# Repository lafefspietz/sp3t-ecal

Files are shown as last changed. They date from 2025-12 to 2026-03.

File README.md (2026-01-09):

# [sp3t-ecal](https://github.com/lafefspietz/sp3t-ecal)

Open source MEMS-based single pole three throw circuit board with improved impedance matching and SMA launches. This is in a rough draft status now, and is in active development.  This is to become a part of a system which will have two of these switch boards and a set of breakout baords for connecting the DC control lines to these RF switch boards, and to then connect to the 25 pin mirco D which is standard in most cryogenic systems used for superconducting quantum systems. Board is 50 mm square. 
 
 - [SP3TECAL.kicad_sch](SP3TECAL.kicad_sch)
 - [SP3TECAL.kicad_pcb](SP3TECAL.kicad_pcb)
 - [SP3TECAL.kicad_pro](SP3TECAL.kicad_pro)
 - [MM5230-03NDB-TR.lib](MM5230-03NDB-TR.lib)
 - [lafe_spietz_library.kicad_sym](lafe_spietz_library.kicad_sym)

## Screen shot of schematic draft:

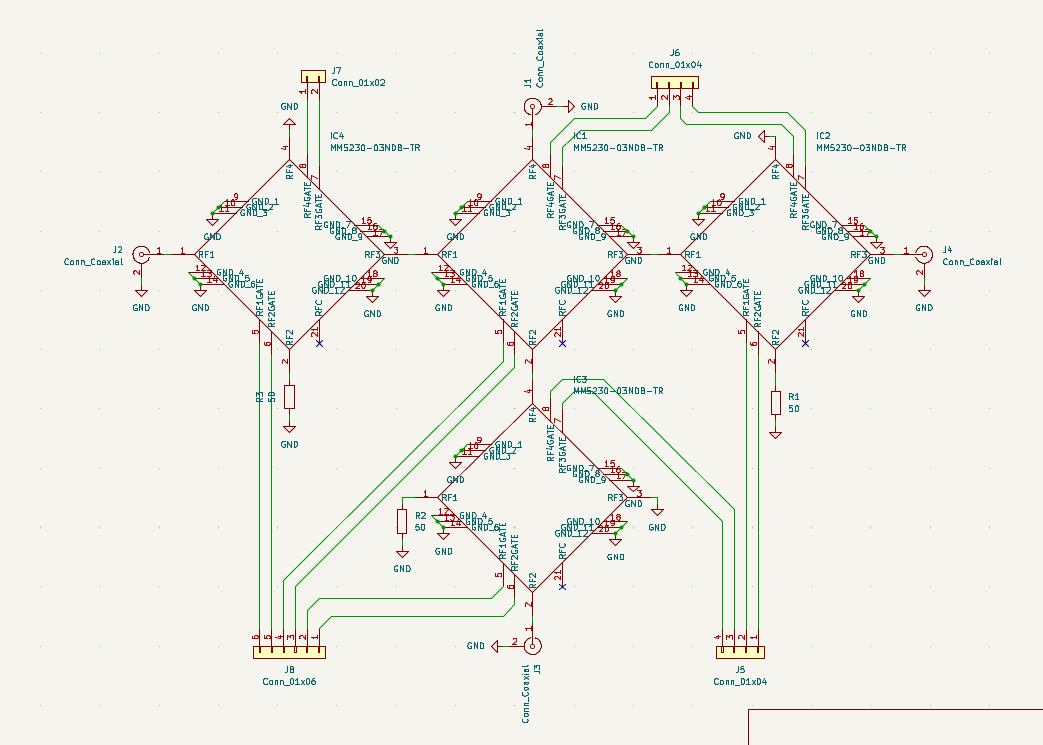
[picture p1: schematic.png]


## Screen shot of layout draft:

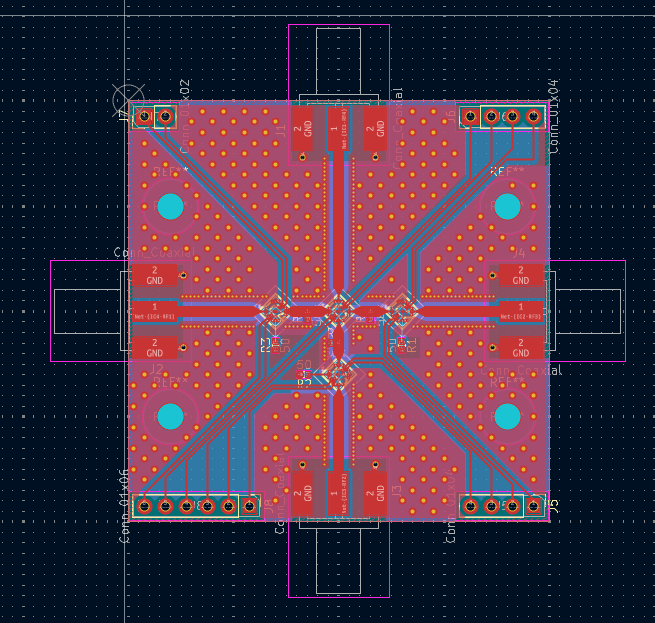
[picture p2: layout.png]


## Screen shot of 3d:

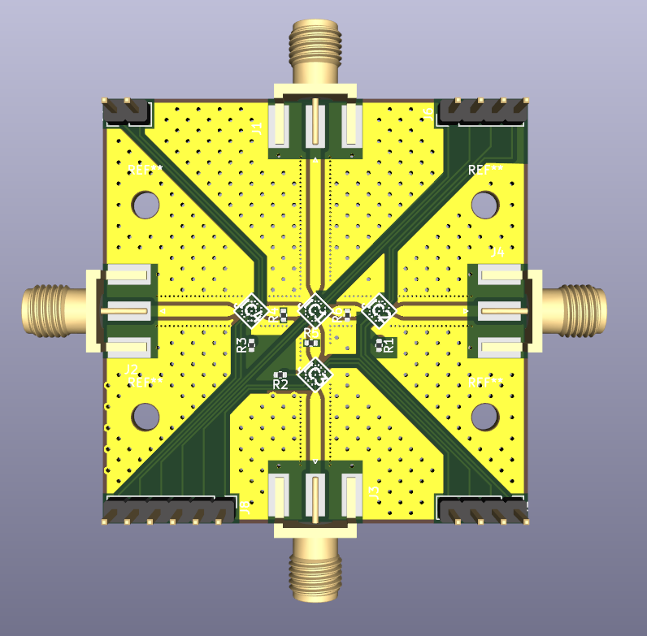
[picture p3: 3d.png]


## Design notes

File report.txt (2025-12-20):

Info: Processing symbol 'IC1:mm5230:MM523003NDB'.
Info: Processing symbol 'IC4:mm5230:MM523003NDB'.
Info: Processing symbol 'IC3:mm5230:MM523003NDB'.
Info: Processing symbol 'IC2:mm5230:MM523003NDB'.
Info: Processing symbol 'J1:Connector_Coaxial:SMA_Molex_73251-1153_EdgeMount_Horizontal'.
Info: Processing symbol 'J2:Connector_Coaxial:SMA_Molex_73251-1153_EdgeMount_Horizontal'.
Info: Processing symbol 'J3:Connector_Coaxial:SMA_Molex_73251-1153_EdgeMount_Horizontal'.
Info: Processing symbol 'J4:Connector_Coaxial:SMA_Molex_73251-1153_EdgeMount_Horizontal'.
Info: Processing symbol 'J5:Connector_PinHeader_2.54mm:PinHeader_1x04_P2.54mm_Vertical'.
Info: Total warnings: 0, errors: 0.
Info: Processing symbol 'J6:Connector_PinHeader_2.54mm:PinHeader_1x04_P2.54mm_Vertical'.
Info: Processing symbol 'J7:Connector_PinHeader_2.54mm:PinHeader_1x02_P2.54mm_Vertical'.
Info: Processing symbol 'J8:Connector_PinHeader_2.54mm:PinHeader_1x06_P2.54mm_Vertical'.
Info: Processing symbol 'R1:Resistor_SMD:R_0402_1005Metric'.
Info: Processing symbol 'R2:Resistor_SMD:R_0402_1005Metric'.
Info: Processing symbol 'R3:Resistor_SMD:R_0402_1005Metric'.
Add net unconnected-(IC1-RFC-Pad21).
Connected IC1 pin 21 to unconnected-(IC1-RFC-Pad21).
Connected IC1 pin 20 to GND.
Connected IC1 pin 15 to GND.
Connected IC1 pin 12 to GND.
Connected IC1 pin 13 to GND.
Connected IC1 pin 11 to GND.
Add net Net-(IC1-RF4).
Connected IC1 pin 4 to Net-(IC1-RF4).
Connected IC1 pin 9 to GND.
Connected IC1 pin 16 to GND.
Add net Net-(IC1-RF2GATE).
Connected IC1 pin 6 to Net-(IC1-RF2GATE).
Add net Net-(IC1-RF1).
Connected IC1 pin 1 to Net-(IC1-RF1).
Connected IC1 pin 19 to GND.
Connected IC1 pin 10 to GND.
Add net Net-(IC1-RF4GATE).
Connected IC1 pin 8 to Net-(IC1-RF4GATE).
Add net Net-(IC1-RF1GATE).
Connected IC1 pin 5 to Net-(IC1-RF1GATE).
Add net Net-(IC1-RF3GATE).
Connected IC1 pin 7 to Net-(IC1-RF3GATE).
Connected IC1 pin 18 to GND.
Add net Net-(IC1-RF2).
Connected IC1 pin 2 to Net-(IC1-RF2).
Connected IC1 pin 14 to GND.
Added IC2 (footprint 'mm5230:MM523003NDB').
Changed IC** reference designator to IC2.
Changed IC2 value from MM523003NDB to MM5230-03NDB-TR.
Updated IC2 symbol association from  to /79b07022-50ec-483d-a1f6-b503f59ca772.
Updated IC2 fields.
Updated IC2 sheetname to '/'.
Updated IC2 sheetfile to 'SP3TECAL.kicad_sch'.
Connected IC2 pin 4 to GND.
Connected IC2 pin 16 to GND.
Connected IC2 pin 19 to GND.
Connected IC2 pin 15 to GND.
Add net unconnected-(IC2-RFC-Pad21).
Connected IC2 pin 21 to unconnected-(IC2-RFC-Pad21).
Connected IC2 pin 20 to GND.
Connected IC2 pin 11 to GND.
Add net Net-(IC2-RF2).
Connected IC2 pin 2 to Net-(IC2-RF2).
Connected IC2 pin 13 to GND.
Connected IC2 pin 14 to GND.
Connected IC2 pin 18 to GND.
Add net Net-(IC2-RF3).
Connected IC2 pin 3 to Net-(IC2-RF3).
Connected IC2 pin 17 to GND.
Add net Net-(IC2-RF3GATE).
Connected IC2 pin 7 to Net-(IC2-RF3GATE).
Connected IC2 pin 10 to GND.
Connected IC2 pin 1 to Net-(IC1-RF3).
Add net Net-(IC2-RF2GATE).
Connected IC2 pin 6 to Net-(IC2-RF2GATE).
Add net Net-(IC2-RF4GATE).
Connected IC2 pin 8 to Net-(IC2-RF4GATE).
Connected IC2 pin 12 to GND.
Connected IC2 pin 9 to GND.
Add net Net-(IC2-RF1GATE).
Connected IC2 pin 5 to Net-(IC2-RF1GATE).
Added IC3 (footprint 'mm5230:MM523003NDB').
Changed IC** reference designator to IC3.
Changed IC3 value from MM523003NDB to MM5230-03NDB-TR.
Updated IC3 symbol association from  to /29d895dc-ca3d-40d6-80b7-e36e3ef9d1bf.
Updated IC3 fields.
Updated IC3 sheetname to '/'.
Updated IC3 sheetfile to 'SP3TECAL.kicad_sch'.
Add net Net-(IC3-RF4GATE).
Connected IC3 pin 8 to Net-(IC3-RF4GATE).
Connected IC3 pin 15 to GND.
Connected IC3 pin 16 to GND.
Connected IC3 pin 13 to GND.
Connected IC3 pin 19 to GND.
Connected IC3 pin 12 to GND.
Connected IC3 pin 3 to GND.
Connected IC3 pin 4 to Net-(IC1-RF2).
Connected IC3 pin 18 to GND.
Add net Net-(IC3-RF2GATE).
Connected IC3 pin 6 to Net-(IC3-RF2GATE).
Add net Net-(IC3-RF2).
Connected IC3 pin 2 to Net-(IC3-RF2).
Connected IC3 pin 10 to GND.
Add net Net-(IC3-RF1GATE).
Connected IC3 pin 5 to Net-(IC3-RF1GATE).
Add net Net-(IC3-RF3GATE).
Connected IC3 pin 7 to Net-(IC3-RF3GATE).
Connected IC3 pin 20 to GND.
Add net Net-(IC3-RF1).
Connected IC3 pin 1 to Net-(IC3-RF1).
Connected IC3 pin 9 to GND.
Add net unconnected-(IC3-RFC-Pad21).
Connected IC3 pin 21 to unconnected-(IC3-RFC-Pad21).
Connected IC3 pin 11 to GND.
Connected IC3 pin 14 to GND.
Connected IC3 pin 17 to GND.
Added IC4 (footprint 'mm5230:MM523003NDB').
Changed IC** reference designator to IC4.
Changed IC4 value from MM523003NDB to MM5230-03NDB-TR.
Updated IC4 symbol association from  to /b7327a34-0eed-4b77-b203-db41979b9248.
Updated IC4 fields.
Updated IC4 sheetname to '/'.
Updated IC4 sheetfile to 'SP3TECAL.kicad_sch'.
Connected IC4 pin 19 to GND.
Connected IC4 pin 4 to GND.
Add net Net-(IC4-RF1GATE).
Connected IC4 pin 5 to Net-(IC4-RF1GATE).
Connected IC4 pin 3 to Net-(IC1-RF1).
Add net Net-(IC4-RF4GATE).
Connected IC4 pin 8 to Net-(IC4-RF4GATE).
Connected IC4 pin 17 to GND.
Connected IC4 pin 9 to GND.
Connected IC4 pin 15 to GND.
Add net Net-(IC4-RF3GATE).
Connected IC4 pin 7 to Net-(IC4-RF3GATE).
Add net Net-(IC4-RF2).
Connected IC4 pin 2 to Net-(IC4-RF2).
Connected IC4 pin 18 to GND.
Connected IC4 pin 16 to GND.
Connected IC4 pin 10 to GND.
Add net Net-(IC4-RF1).
Connected IC4 pin 1 to Net-(IC4-RF1).
Add net Net-(IC4-RF2GATE).
Connected IC4 pin 6 to Net-(IC4-RF2GATE).
Connected IC4 pin 14 to GND.
Connected IC4 pin 20 to GND.
Add net unconnected-(IC4-RFC-Pad21).
Connected IC4 pin 21 to unconnected-(IC4-RFC-Pad21).
Connected IC4 pin 11 to GND.
Connected IC4 pin 13 to GND.
Connected IC4 pin 12 to GND.
Added J1 (footprint 'Connector_Coaxial:SMA_Molex_73251-1153_EdgeMount_Horizontal').
Changed REF** reference designator to J1.
Changed J1 value from SMA_Molex_73251-1153_EdgeMount_Horizontal to Conn_Coaxial.
Updated J1 symbol association from  to /1ebad846-3966-41b4-8a19-6f6ed71a6a6d.
Updated J1 fields.
Updated J1 sheetname to '/'.
Updated J1 sheetfile to 'SP3TECAL.kicad_sch'.
Updated J1 footprint filters to '*BNC* *SMA* *SMB* *SMC* *Cinch* *LEMO* *UMRF* *MCX* *U.FL*'.
Connected J1 pin 2 to GND.
Connected J1 pin 2 to GND.
Connected J1 pin 2 to GND.
Connected J1 pin 2 to GND.
Connected J1 pin 2 to GND.
Connected J1 pin 2 to GND.
Connected J1 pin 2 to GND.
Connected J1 pin 2 to GND.
Connected J1 pin 2 to GND.
Connected J1 pin 2 to GND.
Connected J1 pin 1 to Net-(IC1-RF4).
Added IC1 (footprint 'mm5230:MM523003NDB').
Added J2 (footprint 'Connector_Coaxial:SMA_Molex_73251-1153_EdgeMount_Horizontal').
Changed REF** reference designator to J2.
Changed J2 value from SMA_Molex_73251-1153_EdgeMount_Horizontal to Conn_Coaxial.
Updated J2 symbol association from  to /27fcea4c-f501-4247-b093-c1d6868e0dde.
Updated J2 fields.
Updated J2 sheetname to '/'.
Updated J2 sheetfile to 'SP3TECAL.kicad_sch'.
Updated J2 footprint filters to '*BNC* *SMA* *SMB* *SMC* *Cinch* *LEMO* *UMRF* *MCX* *U.FL*'.
Connected J2 pin 2 to GND.
Connected J2 pin 2 to GND.
Connected J2 pin 2 to GND.
Connected J2 pin 2 to GND.
Connected J2 pin 2 to GND.
Connected J2 pin 2 to GND.
Connected J2 pin 2 to GND.
Connected J2 pin 2 to GND.
Connected J2 pin 2 to GND.
Connected J2 pin 1 to Net-(IC4-RF1).
Connected J2 pin 2 to GND.
Changed IC** reference designator to IC1.
Added J3 (footprint 'Connector_Coaxial:SMA_Molex_73251-1153_EdgeMount_Horizontal').
Changed REF** reference designator to J3.
Changed J3 value from SMA_Molex_73251-1153_EdgeMount_Horizontal to Conn_Coaxial.
Updated J3 symbol association from  to /f328728a-7887-45c8-b8ee-f8669c214e65.
Updated J3 fields.
Updated J3 sheetname to '/'.
Updated J3 sheetfile to 'SP3TECAL.kicad_sch'.
Updated J3 footprint filters to '*BNC* *SMA* *SMB* *SMC* *Cinch* *LEMO* *UMRF* *MCX* *U.FL*'.
Connected J3 pin 2 to GND.
Connected J3 pin 2 to GND.
Connected J3 pin 2 to GND.
Connected J3 pin 2 to GND.
Connected J3 pin 1 to Net-(IC3-RF2).
Connected J3 pin 2 to GND.
Connected J3 pin 2 to GND.
Connected J3 pin 2 to GND.
Connected J3 pin 2 to GND.
Connected J3 pin 2 to GND.
Connected J3 pin 2 to GND.
Changed IC1 value from MM523003NDB to MM5230-03NDB-TR.
Added J4 (footprint 'Connector_Coaxial:SMA_Molex_73251-1153_EdgeMount_Horizontal').
Changed REF** reference designator to J4.
Changed J4 value from SMA_Molex_73251-1153_EdgeMount_Horizontal to Conn_Coaxial.
Updated J4 symbol association from  to /17036cbb-d227-466a-93ab-07385caff96b.
Updated J4 fields.
Updated J4 sheetname to '/'.
Updated J4 sheetfile to 'SP3TECAL.kicad_sch'.
Updated J4 footprint filters to '*BNC* *SMA* *SMB* *SMC* *Cinch* *LEMO* *UMRF* *MCX* *U.FL*'.
Connected J4 pin 2 to GND.
Connected J4 pin 1 to Net-(IC2-RF3).
Connected J4 pin 2 to GND.
Connected J4 pin 2 to GND.
Connected J4 pin 2 to GND.
Connected J4 pin 2 to GND.
Connected J4 pin 2 to GND.
Connected J4 pin 2 to GND.
Connected J4 pin 2 to GND.
Connected J4 pin 2 to GND.
Connected J4 pin 2 to GND.
Updated IC1 symbol association from  to /3e218a32-2774-4c0f-9027-a97876643703.
Added J5 (footprint 'Connector_PinHeader_2.54mm:PinHeader_1x04_P2.54mm_Vertical').
Changed REF** reference designator to J5.
Changed J5 value from PinHeader_1x04_P2.54mm_Vertical to Conn_01x04.
Updated J5 symbol association from  to /f404436d-3f46-4256-b1c0-3e453a5987af.
Updated J5 fields.
Updated J5 sheetname to '/'.
Updated J5 sheetfile to 'SP3TECAL.kicad_sch'.
Updated J5 footprint filters to 'Connector*:*_1x??_*'.
Updated IC1 fields.
Connected J5 pin 1 to Net-(IC2-RF2GATE).
Connected J5 pin 2 to Net-(IC2-RF1GATE).
Connected J5 pin 3 to Net-(IC3-RF4GATE).
Updated IC1 sheetname to '/'.
Added J6 (footprint 'Connector_PinHeader_2.54mm:PinHeader_1x04_P2.54mm_Vertical').
Changed REF** reference designator to J6.
Changed J6 value from PinHeader_1x04_P2.54mm_Vertical to Conn_01x04.
Updated J6 symbol association from  to /832f210d-ca62-42c9-ae07-b18432986929.
Updated J6 fields.
Updated J6 sheetname to '/'.
Updated J6 sheetfile to 'SP3TECAL.kicad_sch'.
Updated J6 footprint filters to 'Connector*:*_1x??_*'.
Connected J6 pin 1 to Net-(IC1-RF4GATE).
Connected J6 pin 3 to Net-(IC2-RF4GATE).
Connected J6 pin 4 to Net-(IC2-RF3GATE).
Connected J6 pin 2 to Net-(IC1-RF3GATE).
Updated IC1 sheetfile to 'SP3TECAL.kicad_sch'.
Added J7 (footprint 'Connector_PinHeader_2.54mm:PinHeader_1x02_P2.54mm_Vertical').
Changed REF** reference designator to J7.
Changed J7 value from PinHeader_1x02_P2.54mm_Vertical to Conn_01x02.
Updated J7 symbol association from  to /74eb3e15-3037-411f-b4f9-73643c7e07a5.
Updated J7 fields.
Updated J7 sheetname to '/'.
Updated J7 sheetfile to 'SP3TECAL.kicad_sch'.
Updated J7 footprint filters to 'Connector*:*_1x??_*'.
Connected J7 pin 2 to Net-(IC4-RF3GATE).
Connected J7 pin 1 to Net-(IC4-RF4GATE).
Add net GND.
Added J8 (footprint 'Connector_PinHeader_2.54mm:PinHeader_1x06_P2.54mm_Vertical').
Changed REF** reference designator to J8.
Changed J8 value from PinHeader_1x06_P2.54mm_Vertical to Conn_01x06.
Updated J8 symbol association from  to /dd451948-362f-4ec4-93f2-a2060d5020ad.
Updated J8 fields.
Updated J8 sheetname to '/'.
Updated J8 sheetfile to 'SP3TECAL.kicad_sch'.
Updated J8 footprint filters to 'Connector*:*_1x??_*'.
Connected J8 pin 3 to Net-(IC1-RF2GATE).
Connected J8 pin 6 to Net-(IC4-RF1GATE).
Connected J5 pin 4 to Net-(IC3-RF3GATE).
Connected J8 pin 4 to Net-(IC1-RF1GATE).
Connected J8 pin 1 to Net-(IC3-RF2GATE).
Connected J8 pin 5 to Net-(IC4-RF2GATE).
Connected IC1 pin 17 to GND.
Added R1 (footprint 'Resistor_SMD:R_0402_1005Metric').
Changed REF** reference designator to R1.
Changed R1 value from R_0402_1005Metric to 50.
Updated R1 symbol association from  to /fe68d1b0-03de-4320-9143-be0620085d62.
Updated R1 fields.
Updated R1 sheetname to '/'.
Updated R1 sheetfile to 'SP3TECAL.kicad_sch'.
Updated R1 footprint filters to 'R_*'.
Connected R1 pin 1 to Net-(IC2-RF2).
Connected R1 pin 2 to GND.
Add net Net-(IC1-RF3).
Added R2 (footprint 'Resistor_SMD:R_0402_1005Metric').
Changed REF** reference designator to R2.
Changed R2 value from R_0402_1005Metric to 50.
Updated R2 symbol association from  to /e5142d02-0f26-4246-8df4-91b4493c952f.
Updated R2 fields.
Updated R2 sheetname to '/'.
Updated R2 sheetfile to 'SP3TECAL.kicad_sch'.
Updated R2 footprint filters to 'R_*'.
Connected R2 pin 1 to Net-(IC3-RF1).
Connected R2 pin 2 to GND.
Connected IC1 pin 3 to Net-(IC1-RF3).
Added R3 (footprint 'Resistor_SMD:R_0402_1005Metric').
Changed REF** reference designator to R3.
Changed R3 value from R_0402_1005Metric to 50.
Updated R3 symbol association from  to /e06167e5-f170-494d-868d-d268c2671973.
Updated R3 fields.
Updated R3 sheetname to '/'.
Updated R3 sheetfile to 'SP3TECAL.kicad_sch'.
Updated R3 footprint filters to 'R_*'.
Connected R3 pin 1 to GND.
Connected R3 pin 2 to Net-(IC4-RF2).

Connected J8 pin 2 to Net-(IC3-RF1GATE).

Info: Total warnings: 0, errors: 0.

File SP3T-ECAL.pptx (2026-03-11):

## MM4250 Cal PCBs and Dual SP3T Ecal

Lafe Spietz
NIST
Boulder, CO

## CPW-G Rogers 4350 B 0.762 mm (30 mils)

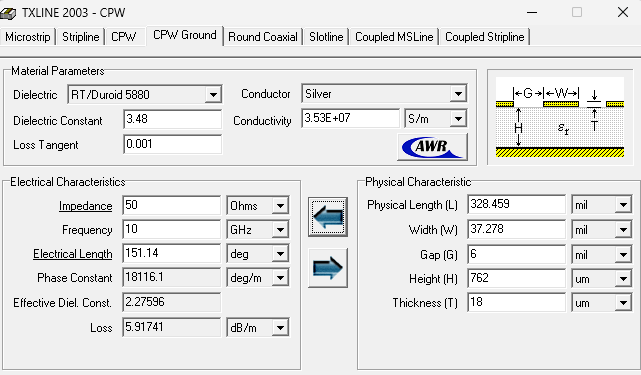
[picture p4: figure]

https://rogerscorp.com/advanced-electronics-solutions/ro4000-series-laminates/ro4350b-laminates

## 60 mil thick board

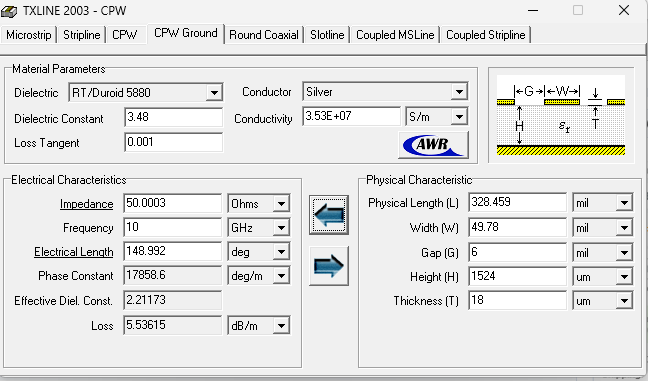
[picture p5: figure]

## Load resistors

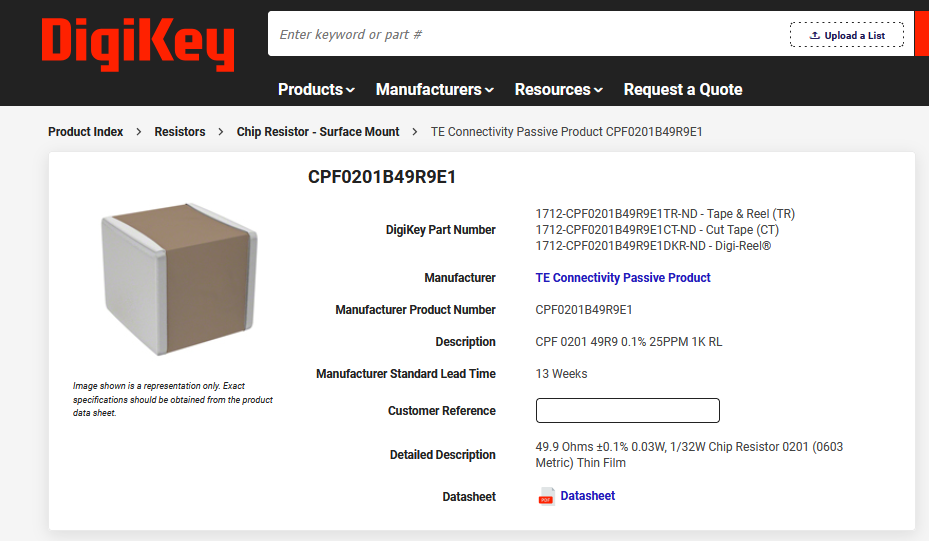
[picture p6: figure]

https://www.digikey.com/en/products/detail/te-connectivity-passive-product/CPF0201B49R9E1/14007284

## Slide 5

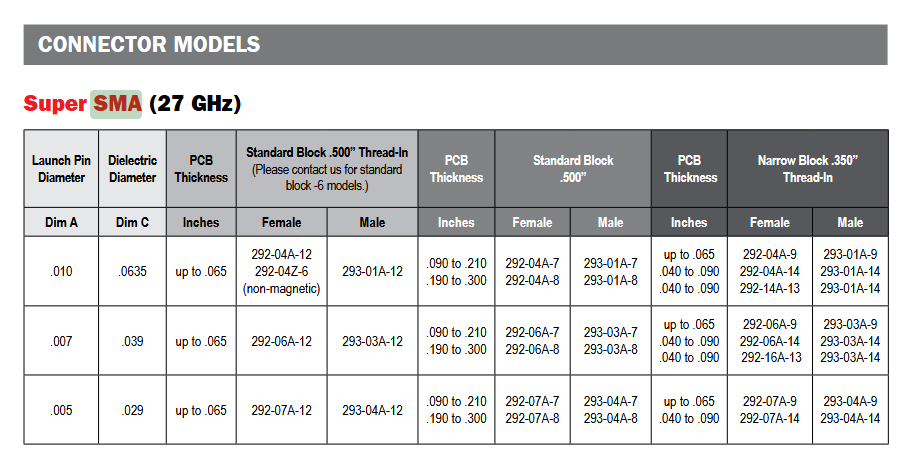
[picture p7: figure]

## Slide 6

https://mpd.southwestmicrowave.com/product/292-04a-12-end-launch-supersma-27-ghz-jack-female-standard-block-500-thread-in/

## SOLT Standards

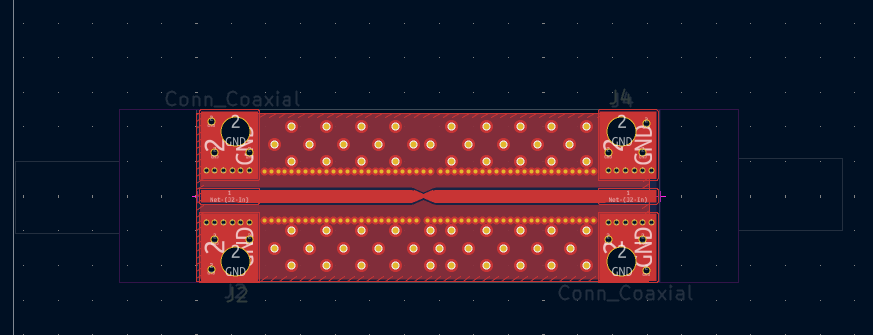
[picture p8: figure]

THRU

SHORT

LOAD

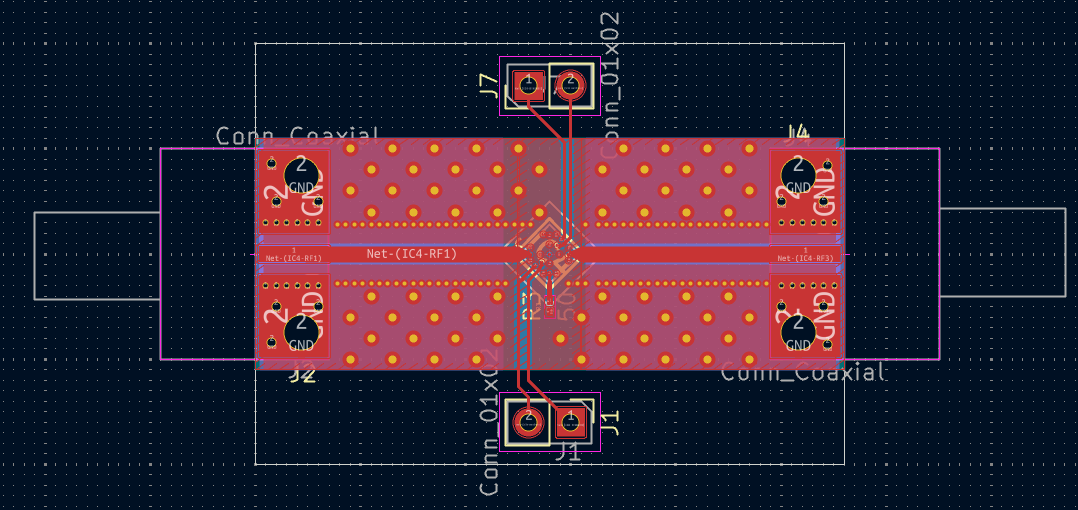
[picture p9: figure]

SWITCH

OPEN

## Dual SP3T Ecal

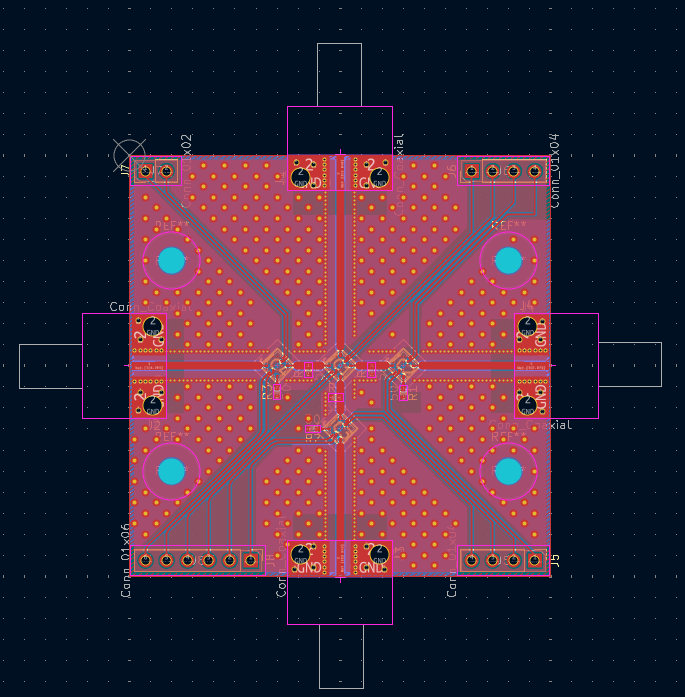
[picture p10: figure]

## Questions

- Do we want to make an attempted impedance transformer to also test?
- Do we want to switch to the full Eurocircuits stackup for the SP3T board?
- Do we want 30 mil or 60 mil boards for the test boards?
- Who orders the boards?
- What else to make?
- What about trying to measure TWPA in existing switch setup? Have they tried it? Should we try it?
- Where to publish results on measurements?

## Impedance matching network, version 1

Input

√((600 pH)/(0.3 pF)) = 44.7 Ω

Switch

0.3 pF

600 pH

## 44.7 Ohm impedance

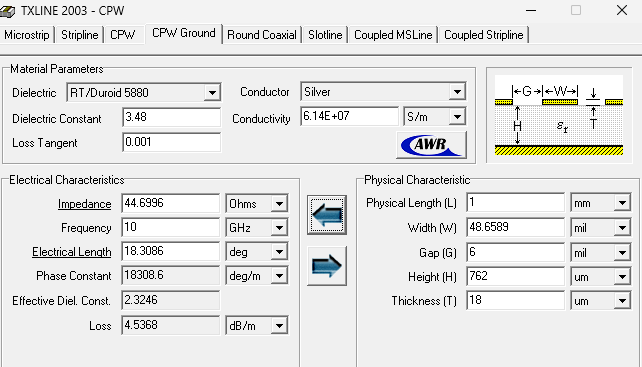
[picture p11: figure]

## We have 4 of these:

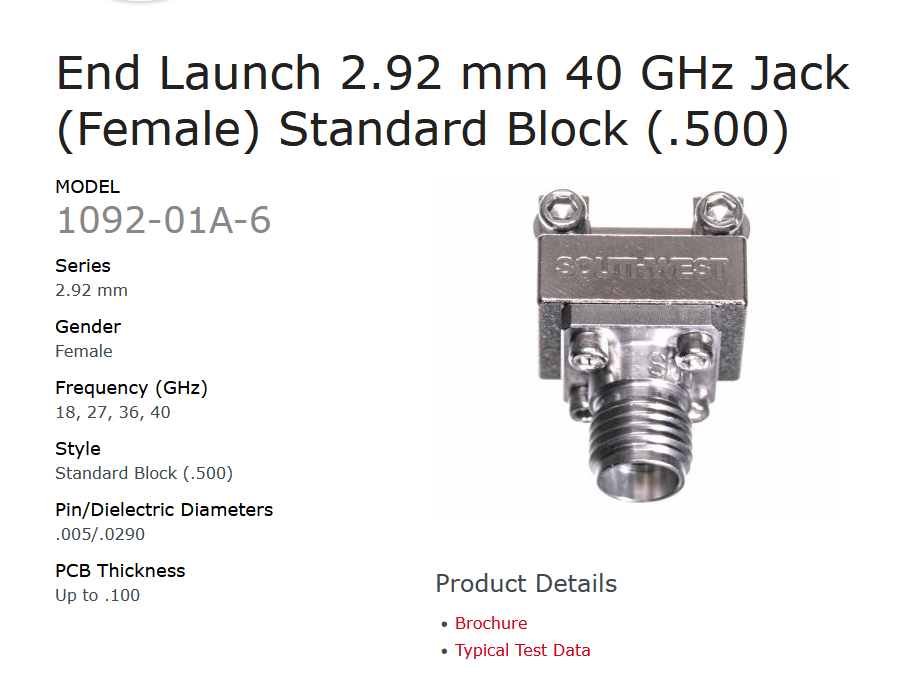
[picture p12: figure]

## TWPA-TRON

SPDT

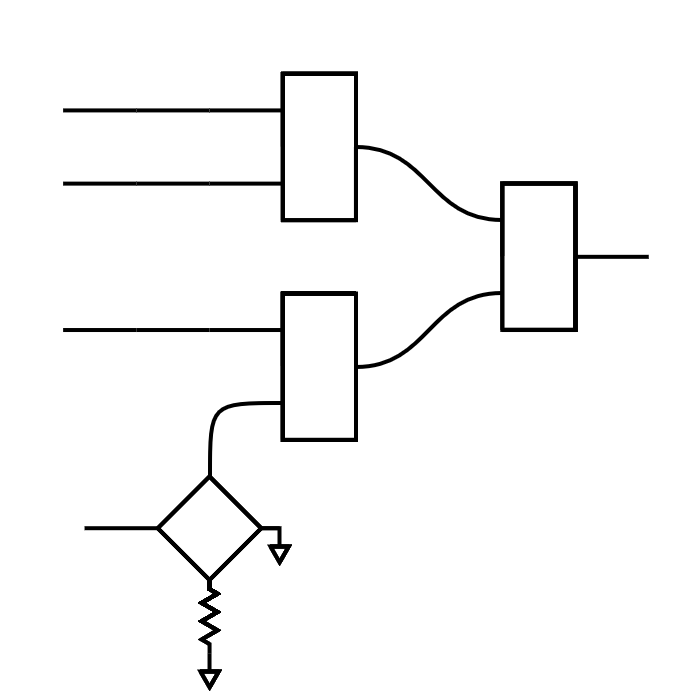
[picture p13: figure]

SPDT

DUT1

SPDT

DUT2

SPDT

SPDT

DUT3

SPDT

SP3T

SP3T

SOLR

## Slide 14

TWPA-TRON

SPDT

DUT1

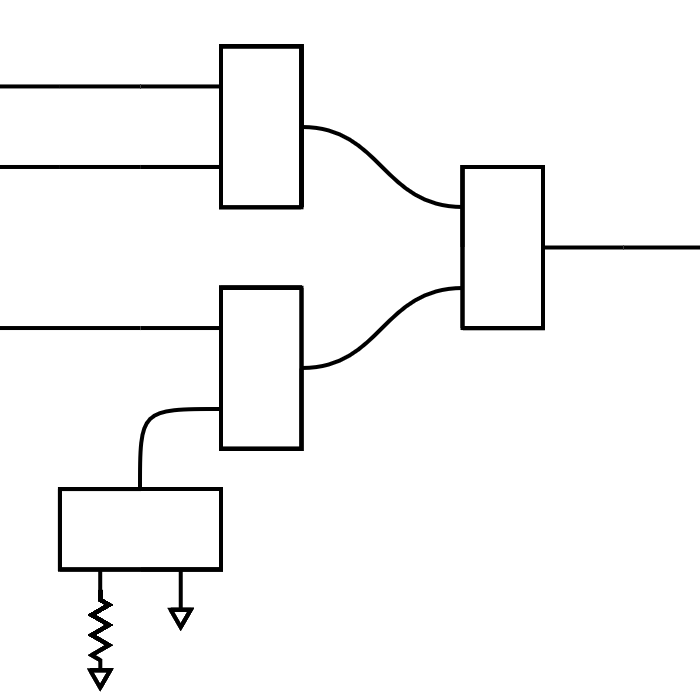
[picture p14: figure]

SPDT

SPDT

DUT2

SPDT

SPDT

SPDT

DUT3

SOL

SPDT

SPDT

SOL

## Rough draft of layout topology

## TWPAtron rough layout topology

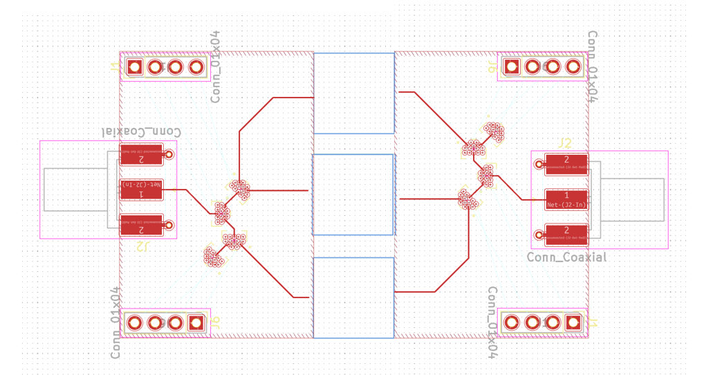
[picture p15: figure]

## TWPAtron Draft

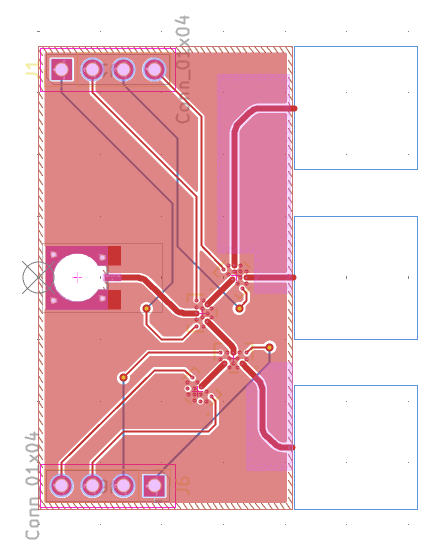
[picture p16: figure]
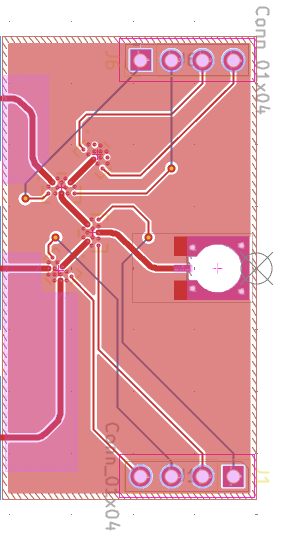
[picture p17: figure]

10x10 mm

## 3d render of latest draft

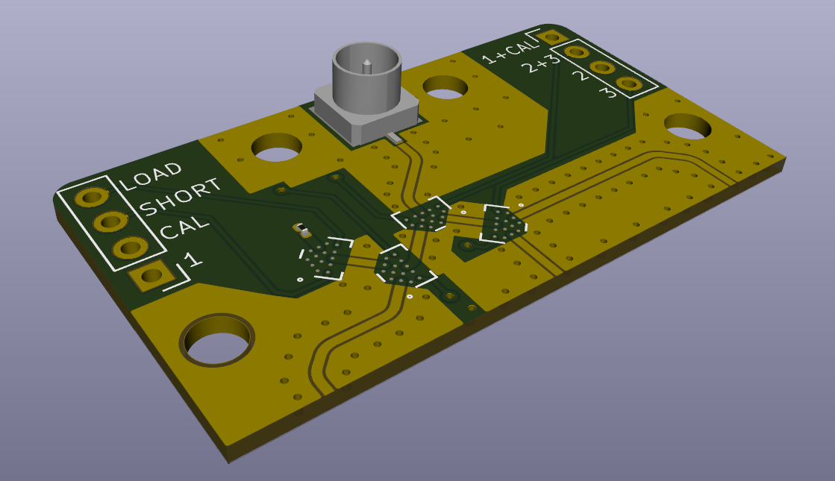
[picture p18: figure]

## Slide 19

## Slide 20

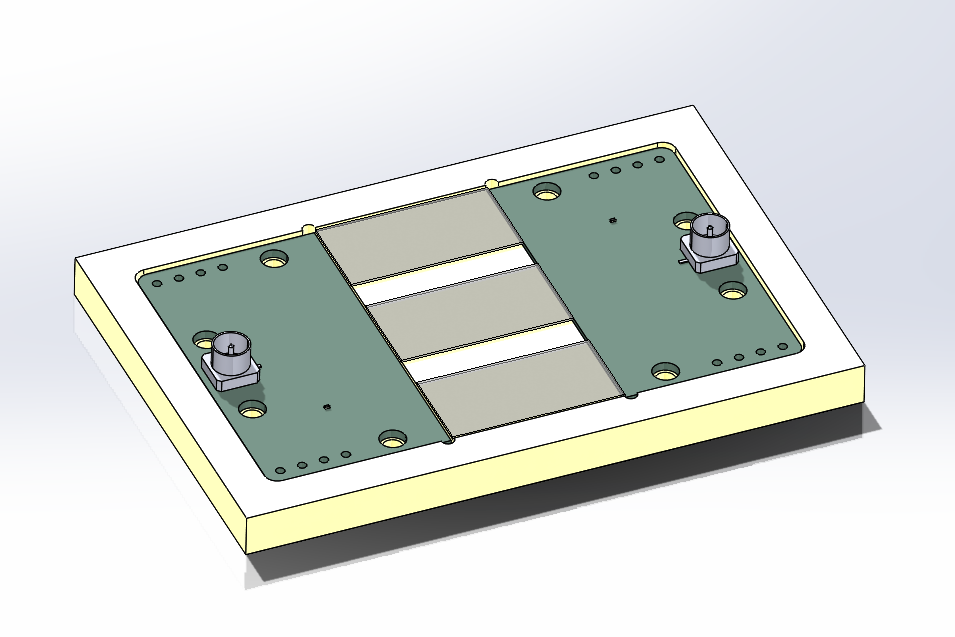
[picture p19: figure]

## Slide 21

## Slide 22

24X65 mil

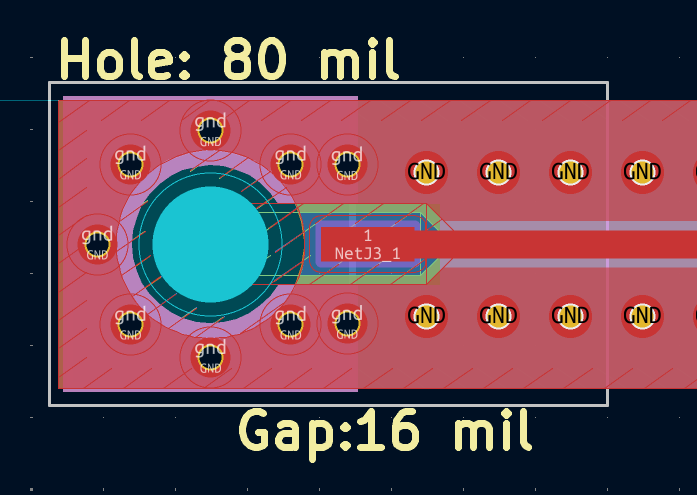
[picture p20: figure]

Diameter 0.131”

Diameter 0.08”

0.085”

0.016”

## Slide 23

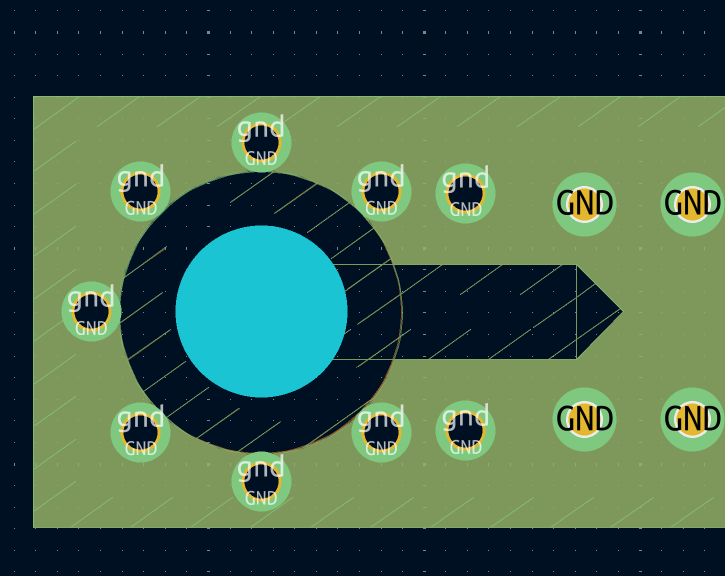
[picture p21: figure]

0.103”

0.044”

## Looking at JAWS designs and Aivon designs

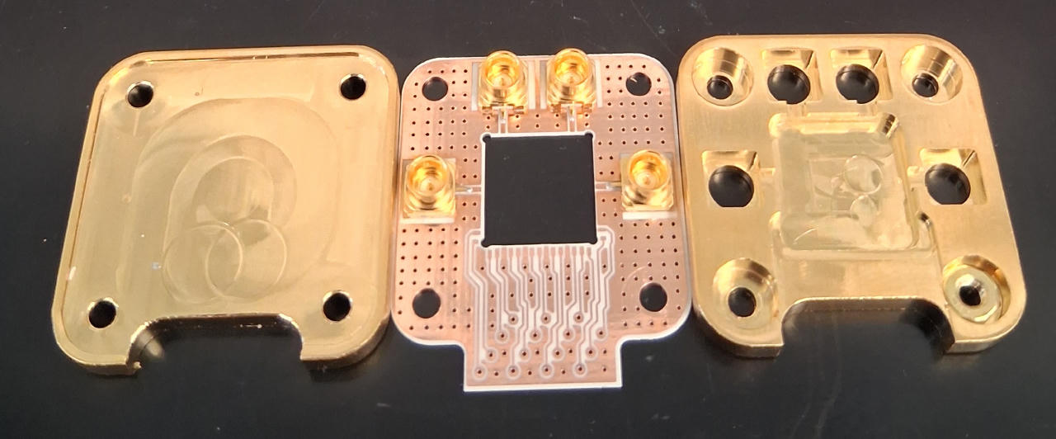
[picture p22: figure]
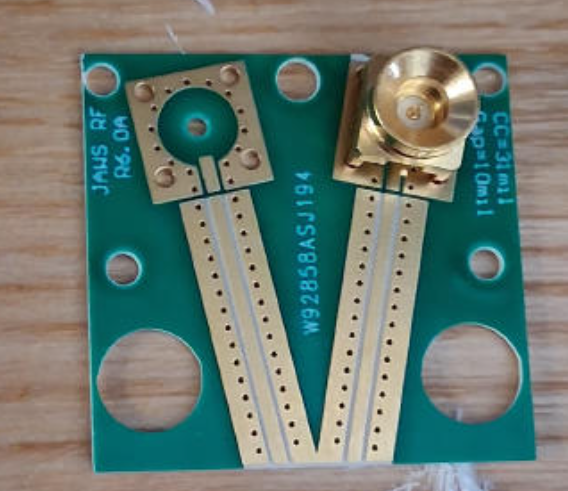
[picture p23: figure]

https://www.digikey.com/en/products/detail/molex/0734153310/2755910

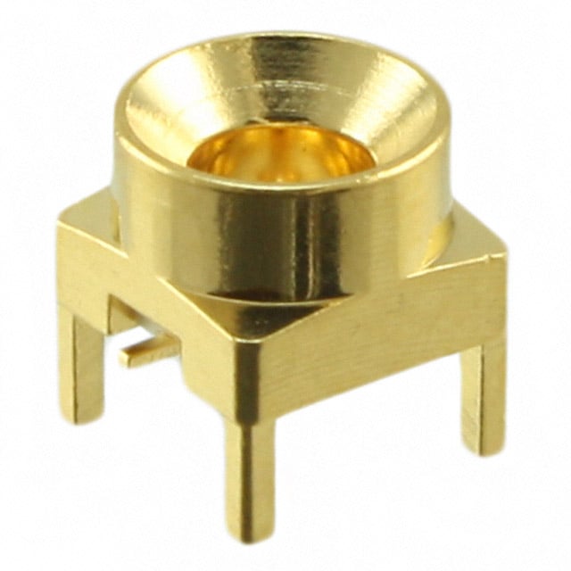
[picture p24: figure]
SMP Connector Plug, Male Pin 50 Ohms Surface Mount Solder

Move to 20 mil PCB
With one insulating layer and 2 copper layers

WM5394CT-ND

## M2.5 Screw and Nut

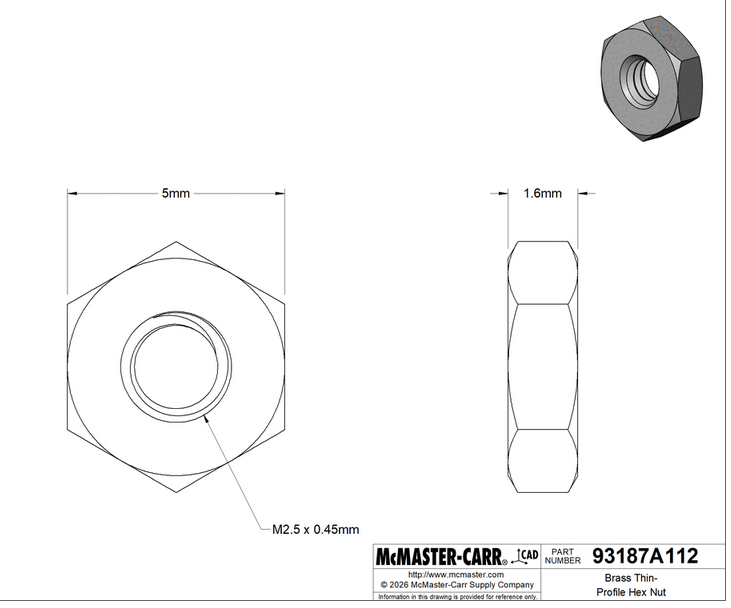
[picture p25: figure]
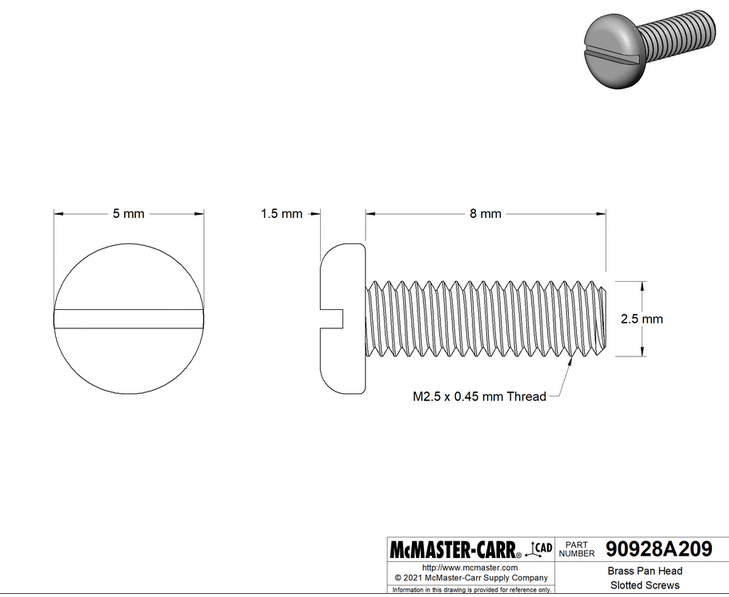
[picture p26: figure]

Clearance 2.75 mm = 108 mils

https://www.mcmaster.com/90928A209/

https://www.mcmaster.com/93187A112/

## JAWS Import from Alium

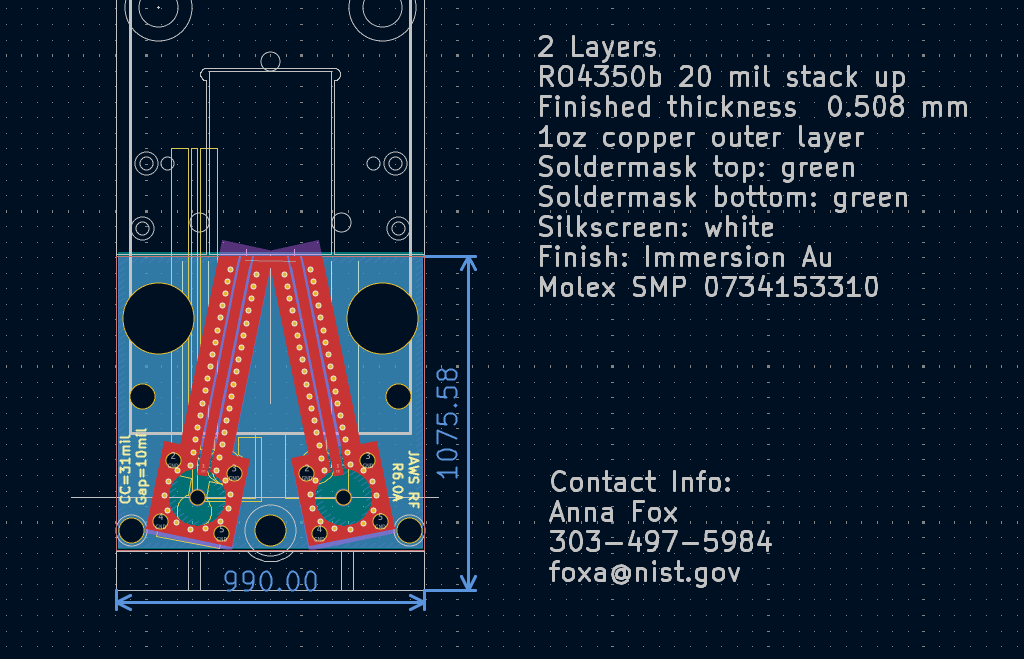
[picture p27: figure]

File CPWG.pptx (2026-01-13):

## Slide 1


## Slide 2

https://rogerscorp.com/advanced-electronics-solutions/ro4000-series-laminates/ro4350b-laminates


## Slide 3


https://mpd.southwestmicrowave.com/wp-content/uploads/End-Launch-Connectors-2024.pdf

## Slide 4


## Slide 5


https://mpd.southwestmicrowave.com/product/292-04a-12-end-launch-supersma-27-ghz-jack-female-standard-block-500-thread-in/

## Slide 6

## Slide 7


https://www.digikey.com/en/products/detail/te-connectivity-linx/CONSMA020-031-G/11482823

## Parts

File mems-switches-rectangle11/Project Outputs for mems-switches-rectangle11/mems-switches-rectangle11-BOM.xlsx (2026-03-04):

Description | Designator | Footprint | Quantity | Mfgr | Mfgr Part No.
DNP | [NoValue], 0 | DNP | 3
DNP | Designator4 | DNP | 1
SMOOTH BORE SMP Connector Plug, Male Pin 50Ohm Surface Mount Solder | J1, J2, J3, J4, J5, J6, J7, J8, J9, J10 | rosenberger-19S201-40ML5 | 10 | Rosenberger | 19S201-40ML5
DNP | J11, J12, J13, J14 | DNP | 4
CPF 0201 56K2 0.1% 25PPM 1K RL | R1, R2, R3, R4, R5, R6, R7, R8, R9, R10, R11, R12 | 0201-resistor | 12 | TE connectivity | CPF0201B56K2E1
High power SP4T MEMs switch | U1, U2, U3, U4 | MM5130-NORM_PCB_NOFLOOD | 4 | Menlo Microwave | MM5130-03NDB-TR

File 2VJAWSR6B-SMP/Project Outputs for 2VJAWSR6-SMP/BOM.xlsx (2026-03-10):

Designator | Qty | Link | MFR | P/N
Designator 19, Designator 20 | 2 | https://www.digikey.com/en/products/detail/molex/0734153310/2755910 | Molex | 734153310

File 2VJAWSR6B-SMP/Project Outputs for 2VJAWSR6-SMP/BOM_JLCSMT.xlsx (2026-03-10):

Comment | Designator | Footprint | JLCPCB Part #（optional）
 | Designator19, Designator20 |  | C5859378

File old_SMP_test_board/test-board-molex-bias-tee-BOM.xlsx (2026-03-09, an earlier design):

Description | Designator | Quantity | Manufacturer Part Number 1 | Mfr_Name | Link
BROADBAND CAPACITOR, 100 nF, 0201 | C1, C2 | 2 | 0201BB104KW160 | Passive Plus | https://www.digikey.com/en/products/detail/passive-plus/0201BB104KW160/19186628
Molex 85305-0232 | J1, J2, J3, J4, J5, J6, J7, J8, J9, J10, J11, J12, J25, J26, J27, J28, J29, J30, J31, J32 | 20 | 85305-0232 | Molex | https://www.digikey.com/en/products/detail/molex/0853050232/2421464
SMP-right-angle-19S201-40ML5 | J13, J14, J15, J16, J17, J18 | 6 | 19S201-40ML5 | Rosenberger | https://www.digikey.com/en/products/detail/rosenberger/19S201-40ML5/7926834
Coilcraft BCR-232 2.35 uH conical inductor | L1, L2, L3 | 3 | BCR-232 | CoilCraft | https://www.coilcraft.com/en-us/products/rf/conical-broadband/0-40-ghz/bcr/bcr-232/

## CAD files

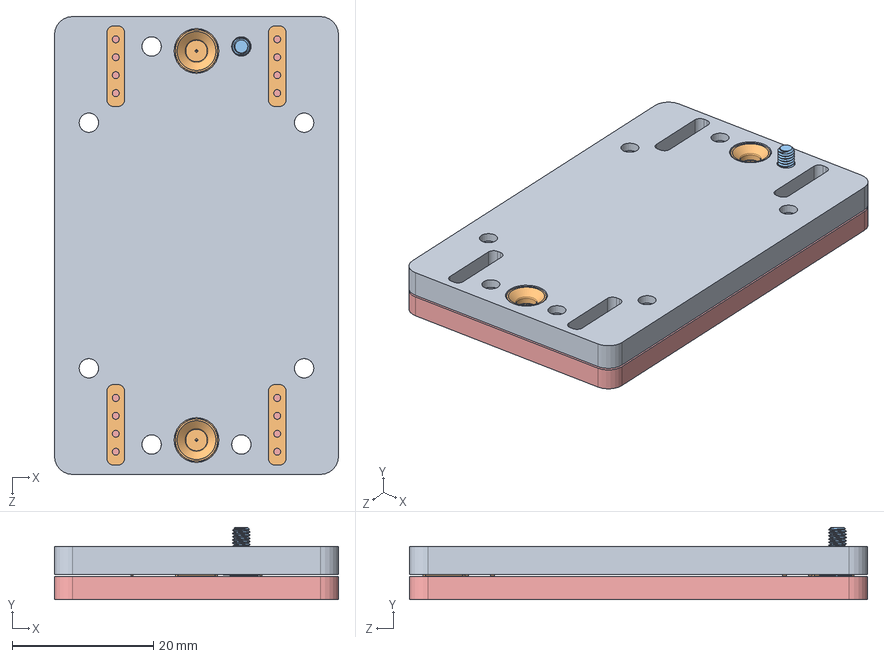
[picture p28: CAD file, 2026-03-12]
twpatron-2-b-assembly.SLDASM
40.2 x 10.3 x 64.8 mm
tpwatron-2-end2
93187A112_Brass Thin-Profile Hex Nut x 2
90928A209_Brass Pan Head Slotted Screws
twpatron-2d x 2
twpatron-lid

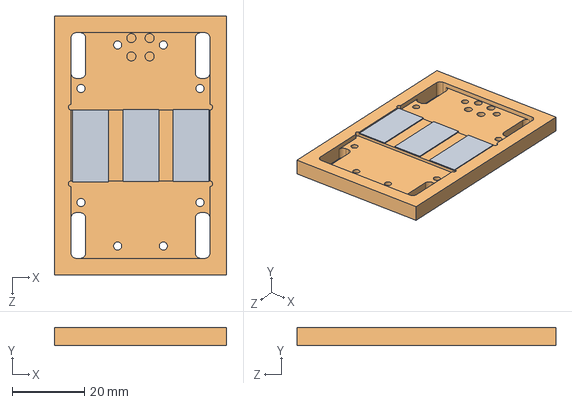
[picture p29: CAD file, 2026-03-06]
twpatron2-Assembly-1.SLDASM
47.8 x 5.00 x 71.8 mm
twpatron-base
chip-10x20 x 3

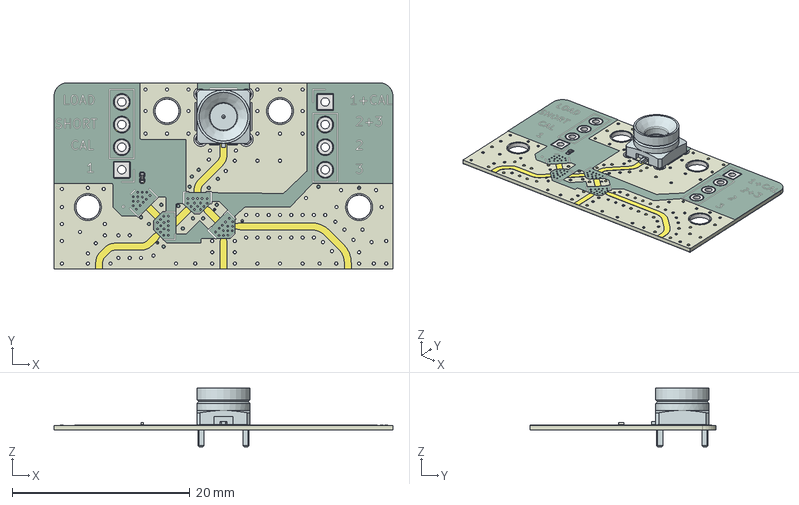
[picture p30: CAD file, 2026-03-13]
twpatron-2e.step
38.1 x 21.0 x 6.60 mm
R_0201_0603Metric
kicad_embedded_6A8167ECC7562BB89ECF910EFD87DB84
twpatron-2_copper
twpatron-2_pad
twpatron-2_via
twpatron-2_silkscreen x 2
twpatron-2_soldermask x 2
twpatron-2_PCB

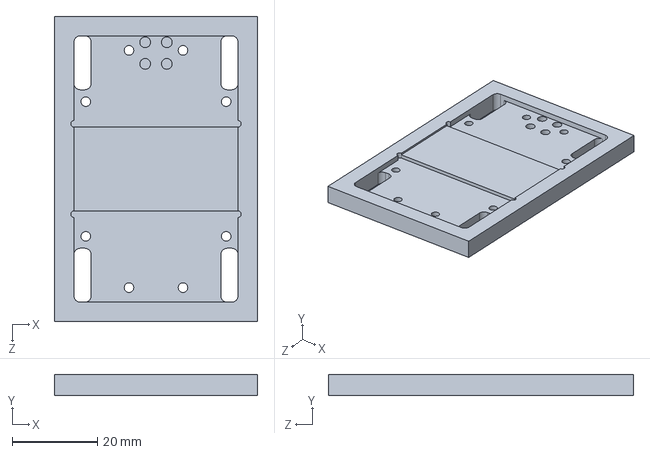
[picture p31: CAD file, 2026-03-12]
twpatron-base.SLDPRT
47.8 x 5.00 x 71.8 mm

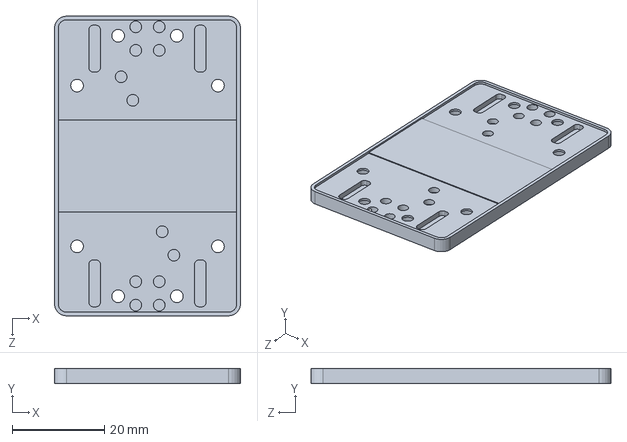
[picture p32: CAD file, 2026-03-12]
tpwatron-2-end2.SLDPRT
40.2 x 3.30 x 64.8 mm

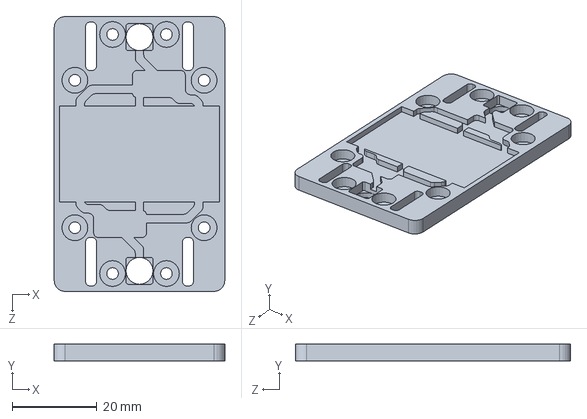
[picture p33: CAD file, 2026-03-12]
twpatron-lid.SLDPRT
40.2 x 3.95 x 64.8 mm

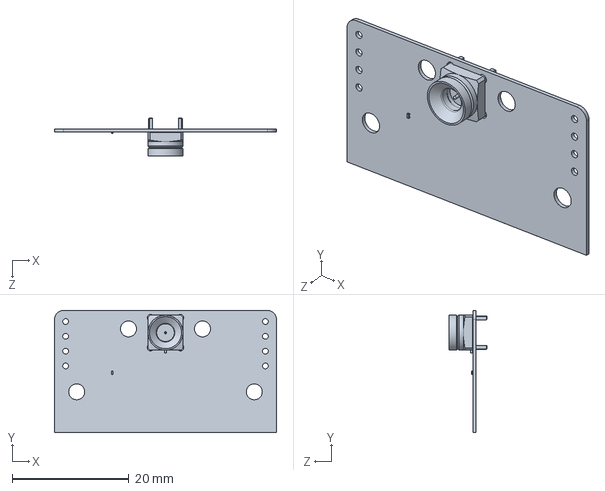
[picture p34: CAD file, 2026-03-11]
twpatron-2b.SLDPRT
38.1 x 21.0 x 6.60 mm

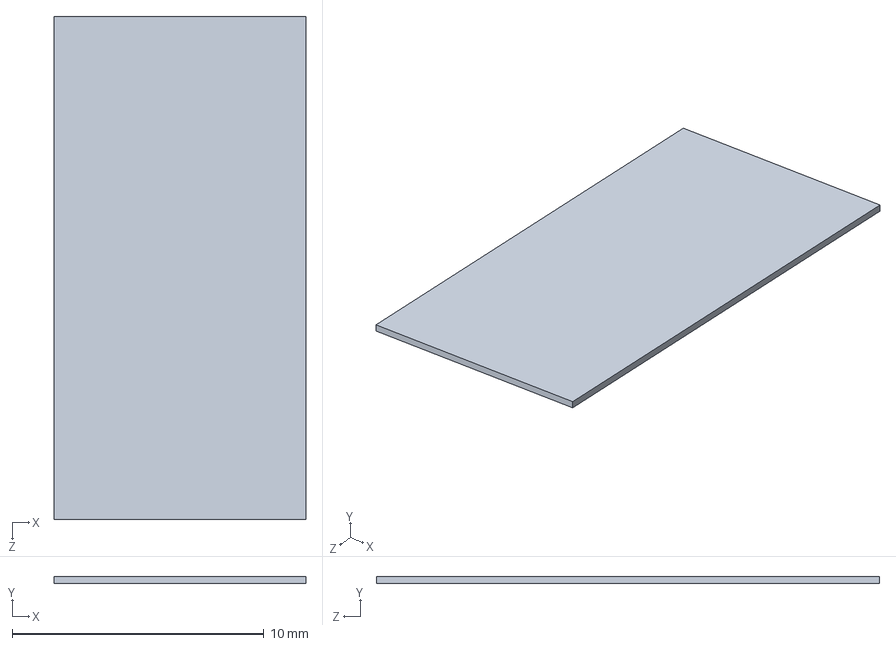
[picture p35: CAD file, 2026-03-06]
chip-10x20.SLDPRT
10.0 x 0.285 x 20.0 mm

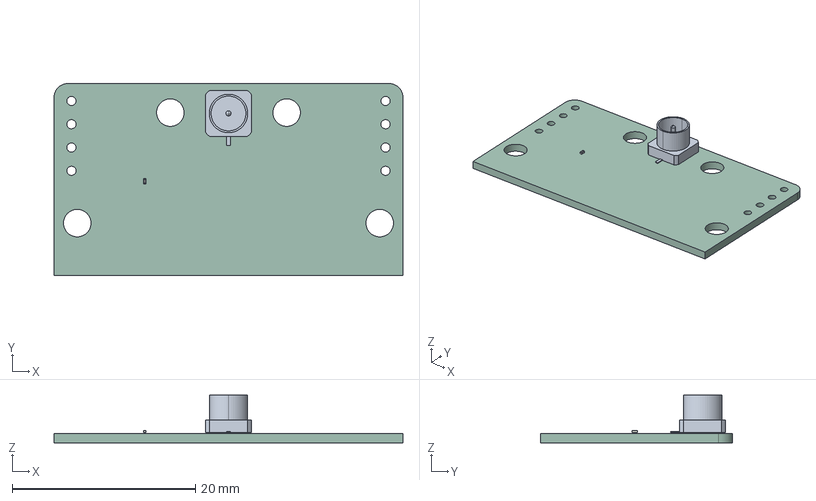
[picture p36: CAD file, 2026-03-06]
twpatron-2.step
38.1 x 21.0 x 5.22 mm
R_0201_0603Metric
kicad_embedded_8CE4FA674CE271D2E1678958DEB25DD1
twpatron-2_PCB

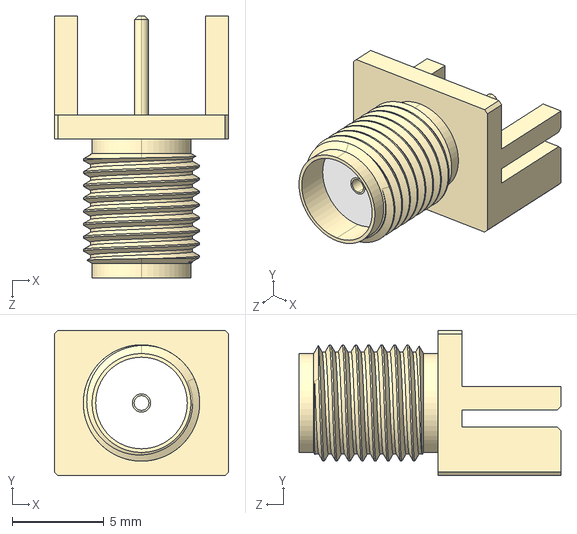
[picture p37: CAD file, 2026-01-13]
CONSMA020.031-G.step
9.52 x 7.92 x 14.3 mm

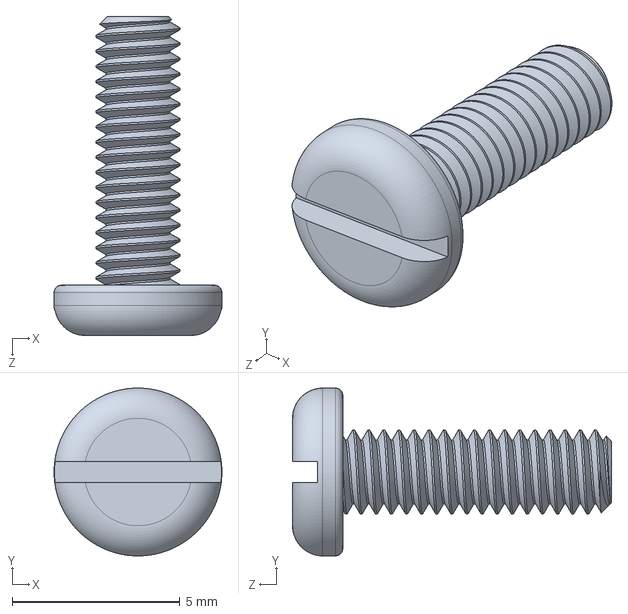
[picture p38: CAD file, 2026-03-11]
90928A209_Brass Pan Head Slotted Screws.SLDPRT
5.00 x 5.00 x 9.50 mm

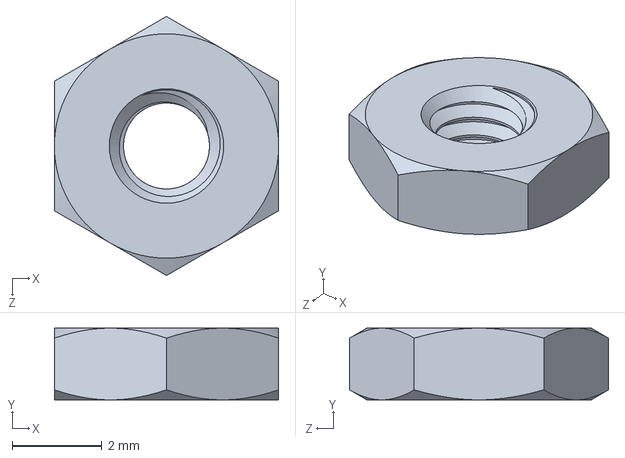
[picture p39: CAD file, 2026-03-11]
93187A112_Brass Thin-Profile Hex Nut.SLDPRT
5.00 x 1.60 x 5.77 mm

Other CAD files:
twpatron-2d.SLDPRT
twpatron-2c.step
twpatron-2-old.SLDPRT
tpwatron-2-end2.SLDDRW
twpatron-2.SLDDRW
twpatron-2.SLDPRT
twpatron-2b.SLDDRW
twpatron-2c.SLDPRT
twpatron-2d.SLDDRW

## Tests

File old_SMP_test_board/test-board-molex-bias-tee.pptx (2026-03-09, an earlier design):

## Test Board Molex And Bias Tee

October 2024
Lafe Spietz et al

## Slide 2

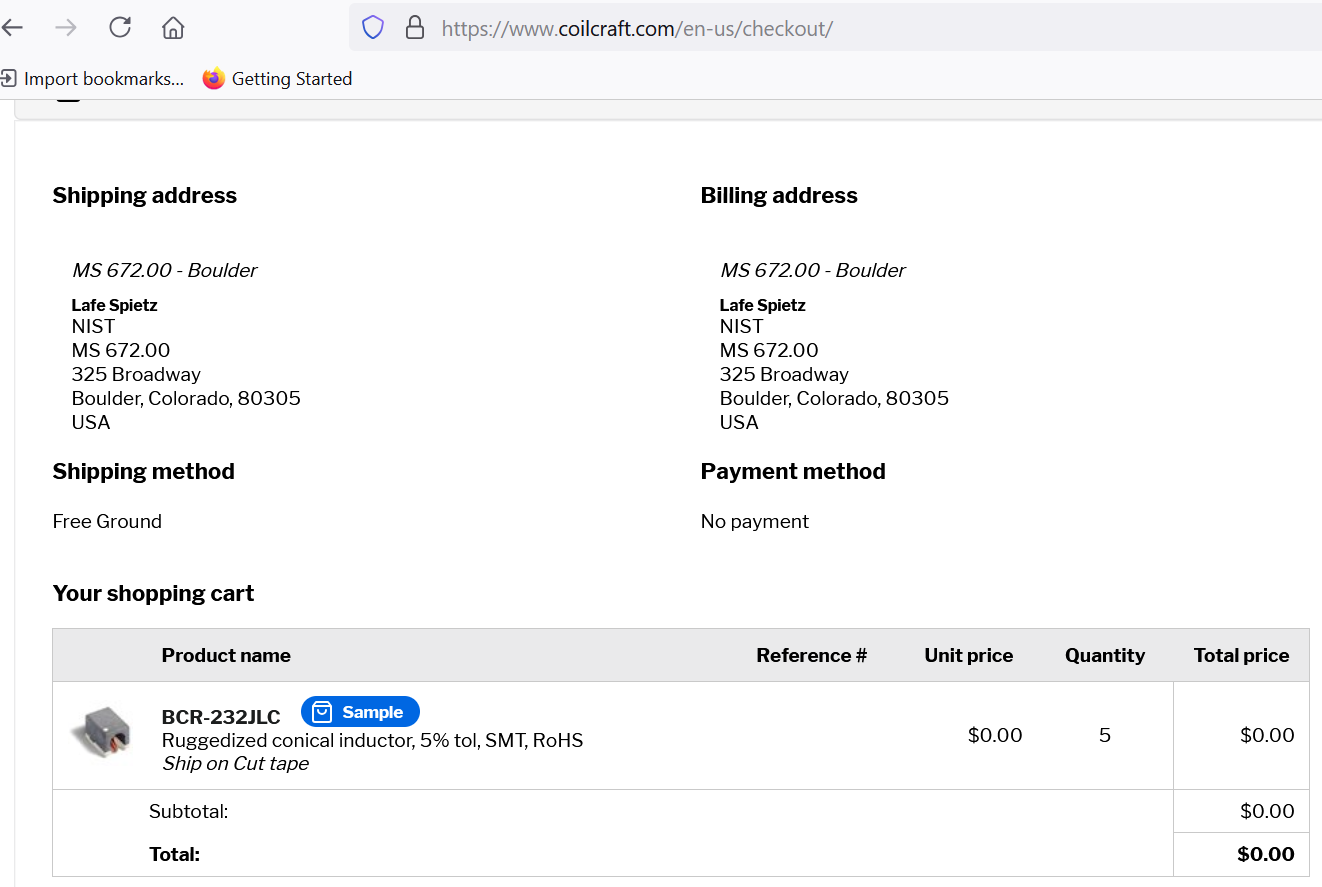
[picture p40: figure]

10/23/24

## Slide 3

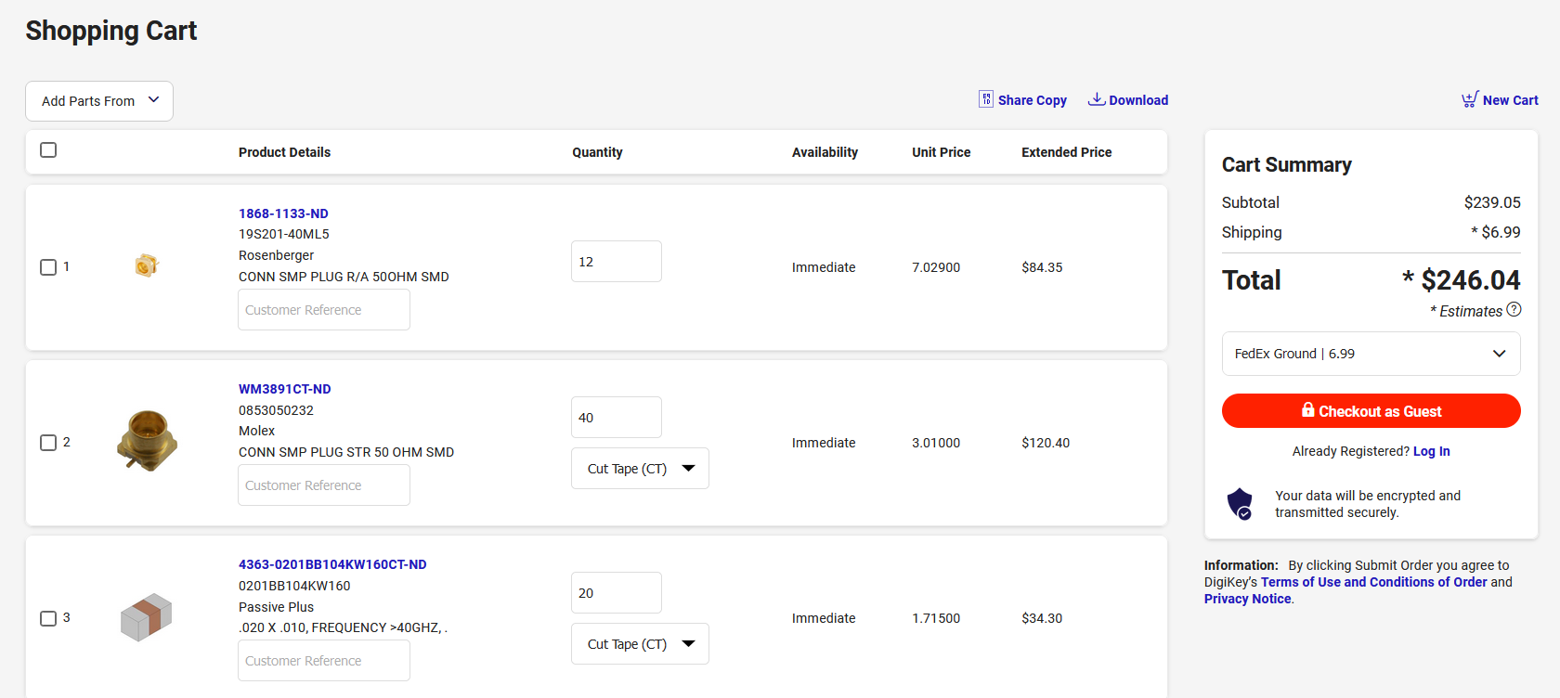
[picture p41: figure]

https://www.digikey.com/short/t1bt58f8

Put into purchasing 10/23/24

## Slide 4

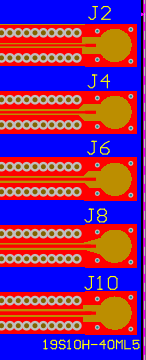
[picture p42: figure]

14 mil center line

16 mil center line

18 mil center line

20 mil center line

22 mil center line

## From thru cal boards:

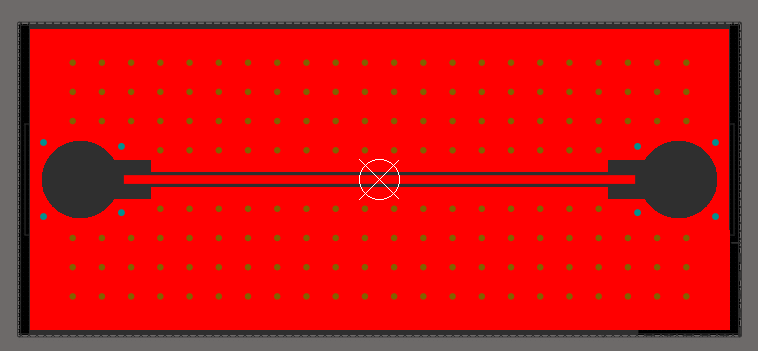
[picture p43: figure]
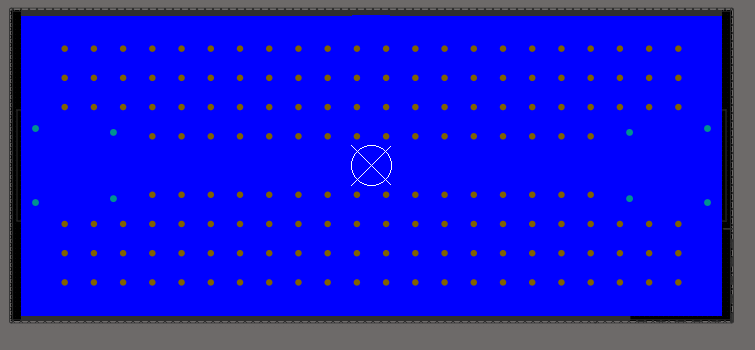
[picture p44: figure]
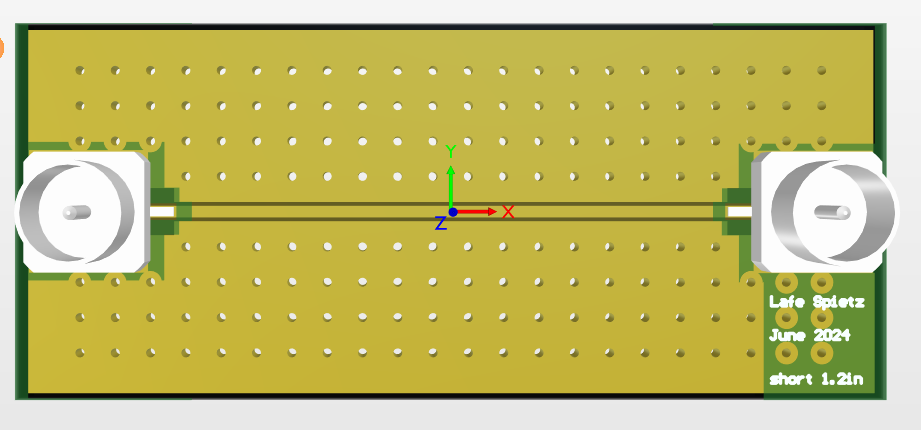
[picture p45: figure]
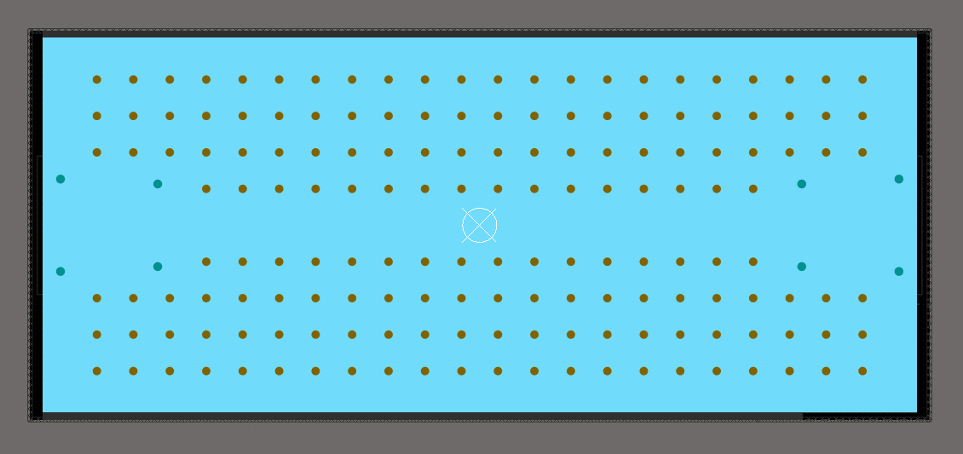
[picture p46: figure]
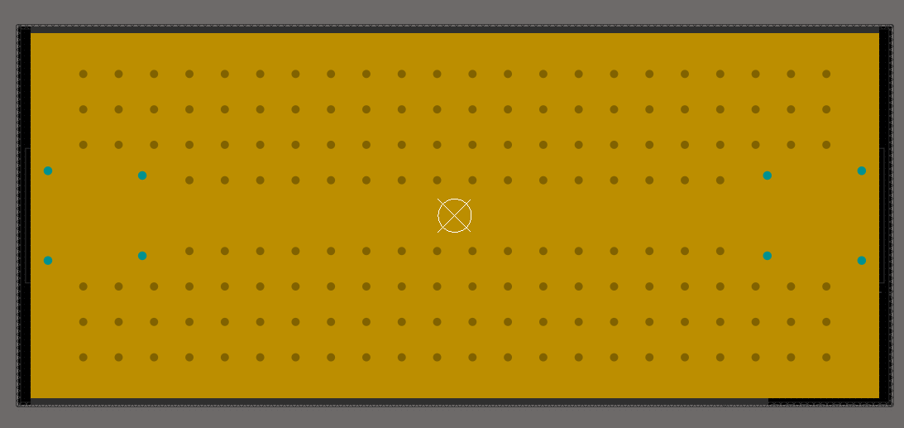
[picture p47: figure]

## What we used in cal boards

Rosenberger 19S141-40ML5

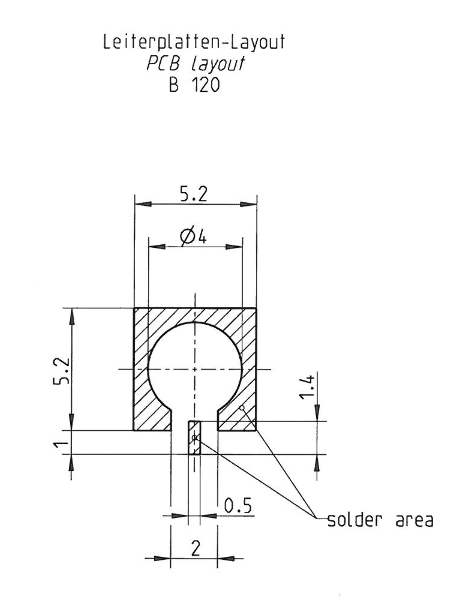
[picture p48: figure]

Terse data sheet, didn’t specify the lower layers of copper or any kind of hole

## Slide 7

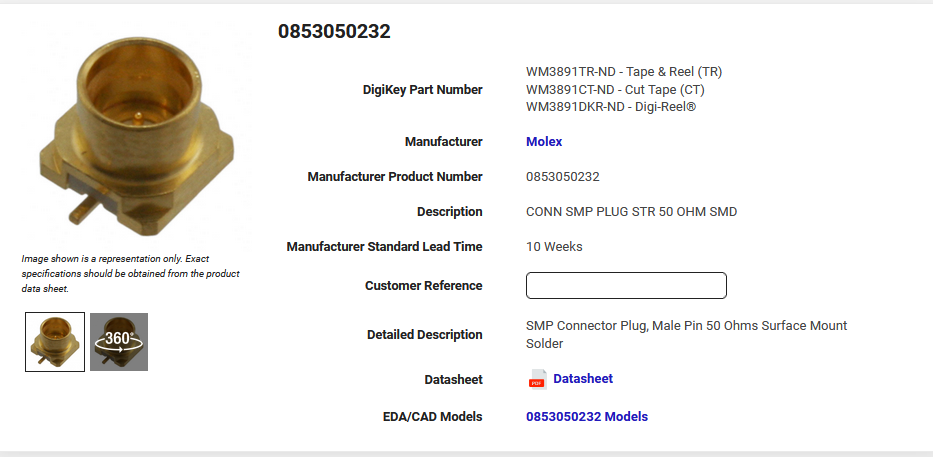
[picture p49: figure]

https://www.digikey.com/en/products/detail/molex/0853050232/2421464

Molex connector chosen by Anna for use on the JAWS project has MUCH more verbose data sheet!

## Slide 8


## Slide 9


## Diameters From data sheet:

- Connector metal outer ring: 177 mils, 4.5 mm
- Soldermask hole: 110 mils, 2.8 mm
- Hole in metal, all 4 layers of metal: 126 mils, 3.2 mm
- Hole in dielectric: 47 mils, 1.19 mm

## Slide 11


https://www.coilcraft.com/en-us/products/rf/conical-broadband/0-40-ghz/bcr/bcr-232/

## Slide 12


## S parameters BCR-232

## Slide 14


https://www.digikey.com/en/products/detail/passive-plus/0201BB104KW160/19186628

Passive Plus 0201BB104KW160
100 nF

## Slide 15


There is a rumor going around that SV microwave is willing to help customers with printed circuit board layout for launch from various connectors. Is this true? We need to launch from a SMP like the 1211-40004 to a grounded coplanar waveguide transmission line on the Eurocircuits RF Pool stackup, with a 6 mil gap, one 10 mil thick layer of RO4350B on each side of the board, and about 19 mils of prepreg in between the inner ground layers, for a total of 4 metal layers. Thanks!

Supposedly SVMicrowave is willing to do design for customers for the launch to various PCB transmission lines.

https://www.svmicrowave.com/smp-male-pcb-surface-mount-connector-ra-ld

## Might be better than coilcraft for availability


https://www.digikey.com/en/products/detail/kyocera-avx/506WLSM0R70KT619T/4789861

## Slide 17


https://www.digikey.com/en/products/detail/kyocera-avx/560W103MTT/22205406

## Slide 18


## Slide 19


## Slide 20


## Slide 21


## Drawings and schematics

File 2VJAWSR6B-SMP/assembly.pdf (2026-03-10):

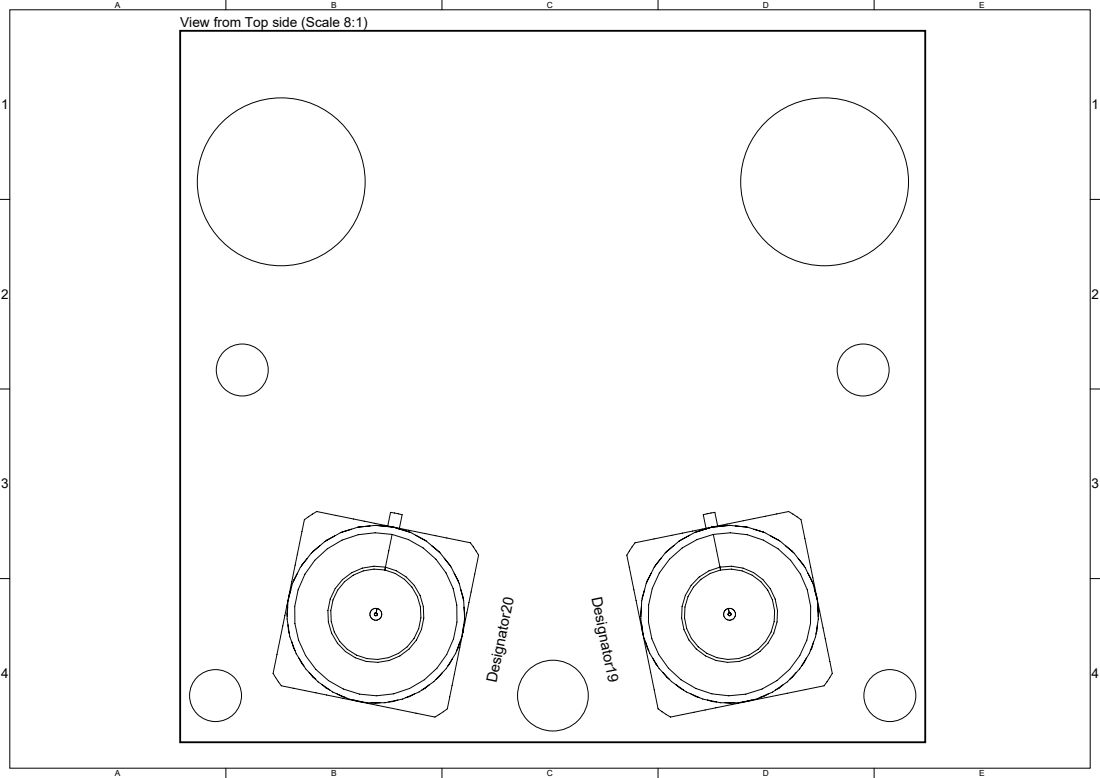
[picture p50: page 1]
Designator20; Designator19

View from Top side (Scale 8:1)

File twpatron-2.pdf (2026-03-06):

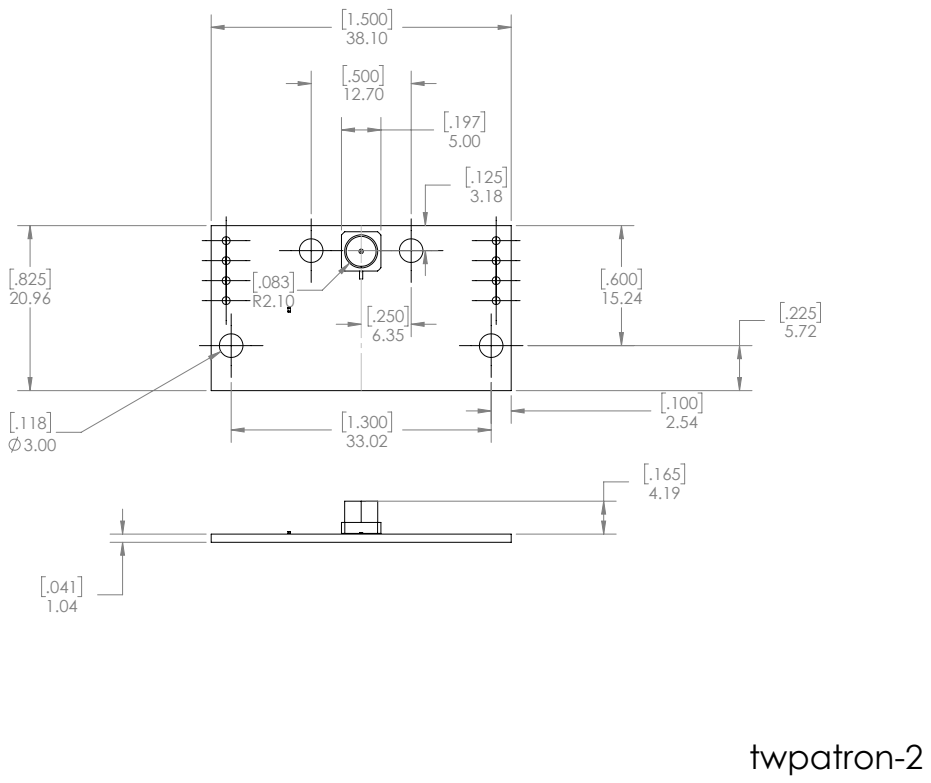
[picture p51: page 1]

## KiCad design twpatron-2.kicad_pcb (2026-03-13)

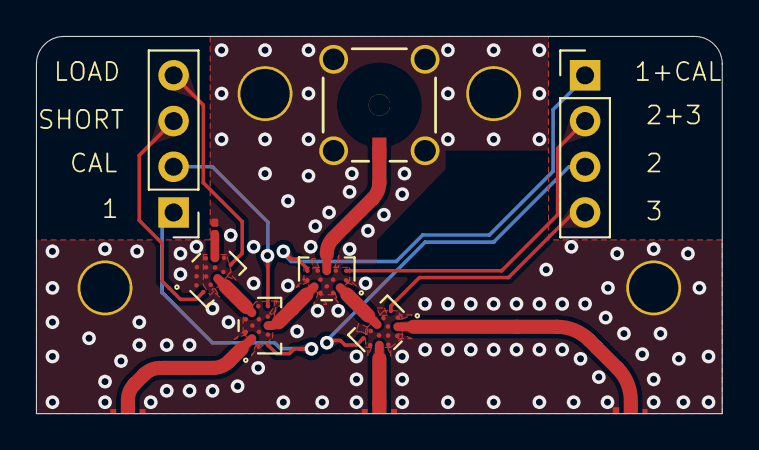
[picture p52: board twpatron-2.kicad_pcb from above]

Board: 2 copper layers, 38.1 x 21.0 mm, 8 parts (0 on the bottom side), 14 nets.

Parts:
J1, J6: Conn_01x04; PinHeader_1x04_P2.54mm_Vertical
J3: SMP-straight-19S141-40ML5; jaws-molex-CONN_73415-3310_MOL
R1: R_US; R_0201_0603Metric
U1, U2, U3, U4: MM5800

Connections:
GND: J3.2, J3.3, J3.4, J3.5, R1.1, U1.A2 (GND), U1.A4 (GND), U1.B1 (GND), U1.B2 (GND), U1.B3 (GND), U1.B4 (GND), U1.C2 (GND), U1.D1 (GND), U1.D2 (GND), U2.A2 (GND), U2.A4 (GND), U2.B1 (GND), U2.B2 (GND), U2.B3 (GND), U2.B4 (GND), U2.C2 (GND), U2.D1 (GND), U2.D2 (GND), U3.A2 (GND), U3.A4 (GND), U3.B1 (GND), U3.B2 (GND), U3.B3 (GND), U3.B4 (GND), U3.C2 (GND), U3.D1 (GND), U3.D2 (GND), U4.A2 (GND), U4.A4 (GND), U4.B1 (GND), U4.B2 (GND), U4.B3 (GND), U4.B4 (GND), U4.C2 (GND), U4.C3 (RF1), U4.D1 (GND), U4.D2 (GND)
unnamed: J1.1, U1.A1 (VG2)
unnamed: J1.2, U1.A5 (VG1)
unnamed: J1.3, U2.A1 (VG2)
unnamed: J1.4, U2.A5 (VG1)
unnamed: J6.1, U3.A5 (VG1)
unnamed: J6.2, U3.A1 (VG2)
unnamed: J6.3, U4.A5 (VG1)
unnamed: J6.4, U4.A1 (VG2)
unnamed: U1.C3 (RF1), U2.A3 (RFC)
unnamed: U1.C1 (RF2), U3.A3 (RFC)
unnamed: J3.1, U1.A3 (RFC)
unnamed: U3.C1 (RF2), U4.A3 (RFC)
unnamed: R1.2, U4.C1 (RF2)

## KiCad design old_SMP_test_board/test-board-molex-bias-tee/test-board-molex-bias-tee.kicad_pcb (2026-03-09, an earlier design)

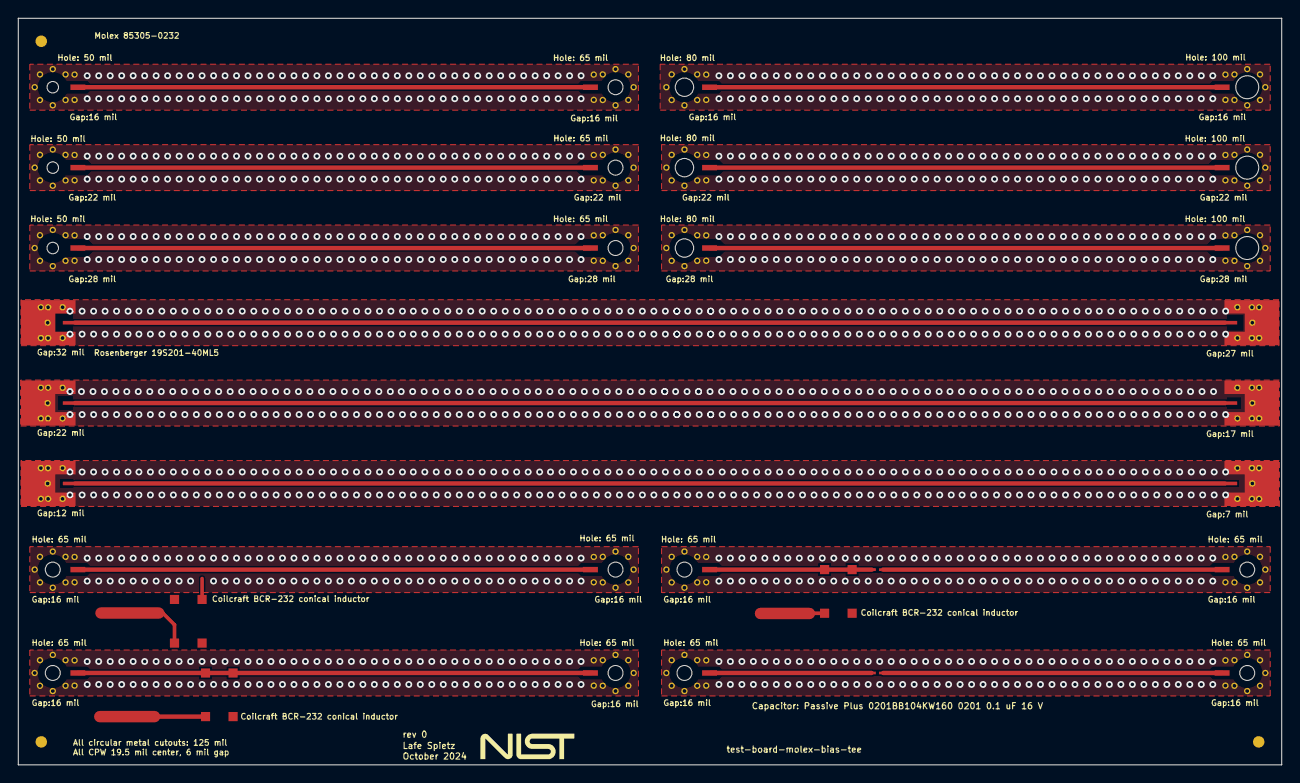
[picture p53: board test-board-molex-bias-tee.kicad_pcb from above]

Board: 4 copper layers, 139.7 x 82.6 mm, 35 parts (0 on the bottom side), 16 nets.

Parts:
0, 0#2, 0#3: Fiducial; fiducial
C1, C2: 100 nF; 0201-capacitor
Designator4: Comment; NIST logo - TopOverlay
J1, J2, J3, J4, J5, J6, J7, J8, J9, J10, J11, J12, J25, J26, J27, J28, J29, J30, J31, J32: 85305-0232; MOLEX_85305-0232
J13, J14, J15, J16, J17, J18: SMP-right-angle-19S201-40ML5; rosenberger-19S201-40ML5
L1, L2, L3: Coilcraft BCR-232 conical inductor

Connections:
GND: J1.gnd, J2.gnd, J3.gnd, J4.gnd, J5.gnd, J6.gnd, J7.gnd, J8.gnd, J9.gnd, J10.gnd, J11.gnd, J12.gnd, J13.gnd, J14.gnd, J15.gnd, J16.gnd, J17.gnd, J18.gnd, J25.gnd, J26.gnd, J27.gnd, J28.gnd, J29.gnd, J30.gnd, J31.gnd, J32.gnd
NetC1_1: C1.1, J31.1
NetC1_2: C1.2, J32.1
NetC2_1: C2.1, J27.1, L2.1, L2.*
NetC2_2: C2.2, J28.1
NetJ1_1: J1.1, J2.1
NetJ3_1: J3.1, J4.1
NetJ5_1: J5.1, J6.1
NetJ7_1: J7.1, J8.1
NetJ9_1: J9.1, J10.1
NetJ11_1: J11.1, J12.1
NetJ13_1: J13.1, J14.1
NetJ15_1: J15.1, J16.1
NetJ17_1: J17.1, J18.1
NetJ25_1: J25.1, J26.1, L3.1
NetJ29_1: J29.1, J30.1, L1.1, L1.*

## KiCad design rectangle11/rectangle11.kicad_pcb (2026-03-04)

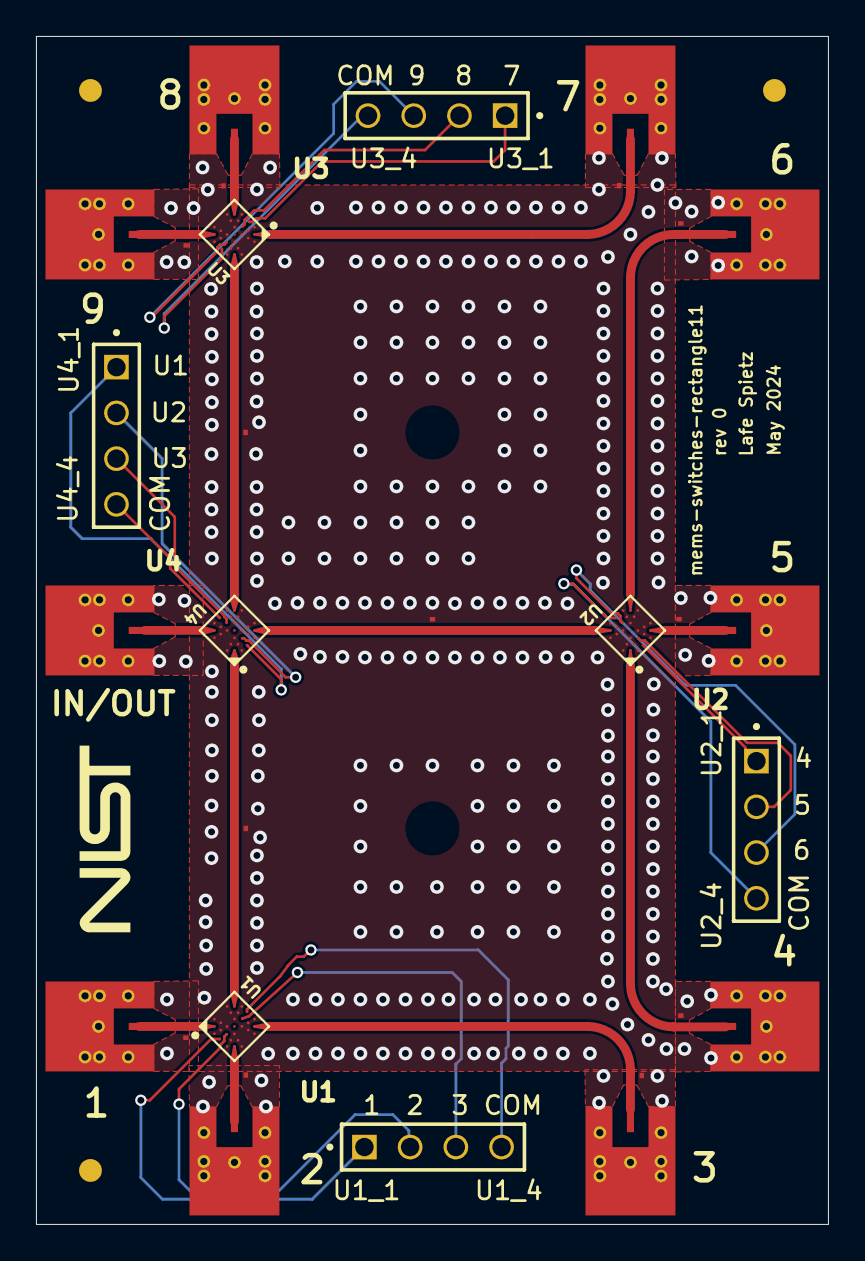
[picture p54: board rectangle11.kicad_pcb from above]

Board: 4 copper layers, 44.0 x 66.0 mm, 32 parts (0 on the bottom side), 30 nets.

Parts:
0: Fiducial; fiducial
Designator4: Comment; NIST logo - TopOverlay
J1, J2, J3, J4, J5, J6, J7, J8, J9, J10: SMP-right-angle-19S201-40ML5; rosenberger-19S201-40ML5
J11, J12, J13, J14: TSW-104-07-G-S; SAMTEC_TSW-104-07-G-S
R1, R2, R3, R4, R5, R6, R7, R8, R9, R10, R11, R12: TE connectivity CPF0201B56K2E1; 0201-resistor
U1, U2, U3, U4: MM5130*; MM5130-NORM_PCB_NOFLOOD

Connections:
GND: J1.gnd, J2.gnd, J3.gnd, J4.gnd, J5.gnd, J6.gnd, J7.gnd, J8.gnd, J9.gnd, J10.gnd, R1.2, R2.2, R3.1, R4.1, R5.1, R6.1, R7.2, R8.2, R9.2, R10.1, R11.2, R12.2, U1.1, U1.3, U1.5, U1.6, U1.8, U1.10, U1.12, U1.13, U1.15, U1.17, U1.18, U1.19, U1.20, U1.22, U1.23, U1.24, U1.25, U1.26, U1.27, U1.28, U2.1, U2.3, U2.5, U2.6, U2.8, U2.10, U2.12, U2.13, U2.15, U2.17, U2.18, U2.19, U2.20, U2.22, U2.23, U2.24, U2.25, U2.26, U2.27, U2.28, U3.1, U3.3, U3.5, U3.6, U3.8, U3.10, U3.12, U3.13, U3.15, U3.17, U3.18, U3.19, U3.20, U3.22, U3.23, U3.24, U3.25, U3.26, U3.27, U3.28, U4.1, U4.3, U4.5, U4.6, U4.8, U4.10, U4.12, U4.13, U4.15, U4.17, U4.18, U4.19, U4.20, U4.22, U4.23, U4.24, U4.25, U4.26, U4.27, U4.28
NetJ1_1: J1.1, R1.1, U1.14
NetJ2_1: J2.1, R2.1, U1.4
NetJ3_1: J3.1, R3.2, U1.7
NetJ4_1: J4.1, R5.2, U2.14
NetJ5_1: J5.1, R6.2, U2.4
NetJ6_1: J6.1, R7.1, U2.7
NetJ7_1: J7.1, R10.2, U3.14
NetJ8_1: J8.1, R12.1, U3.4
NetJ9_1: J9.1, R11.1, U3.7
NetJ10_1: J10.1, U4.11
NetJ11_01: J11.01, U1.2
NetJ11_02: J11.02, U1.16
NetJ11_03: J11.03, U1.21
NetJ11_04: J11.04, U1.9
NetJ12_01: J12.01, U2.2
NetJ12_02: J12.02, U2.16
NetJ12_03: J12.03, U2.21
NetJ12_04: J12.04, U2.9
NetJ13_01: J13.01, U3.2
NetJ13_02: J13.02, U3.16
NetJ13_03: J13.03, U3.21
NetJ13_04: J13.04, U3.9
NetJ14_01: J14.01, U4.2
NetJ14_02: J14.02, U4.16
NetJ14_03: J14.03, U4.21
NetJ14_04: J14.04, U4.9
NetR4_2: R4.2, U1.11, U4.14
NetR8_1: R8.1, U2.11, U4.4
NetR9_1: R9.1, U3.11, U4.7

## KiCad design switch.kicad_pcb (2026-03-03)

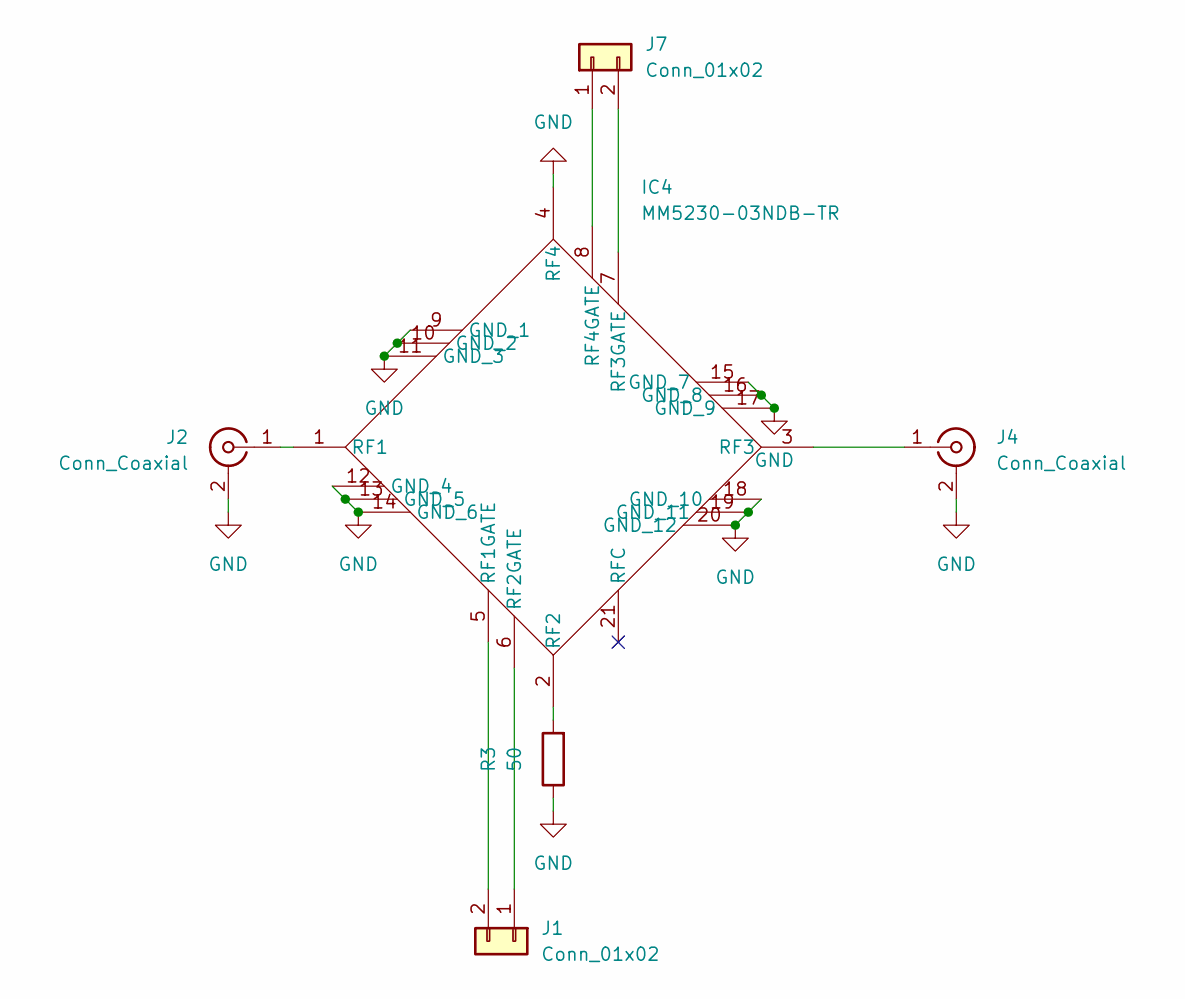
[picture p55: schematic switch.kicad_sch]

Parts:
IC4: MM5230-03NDB-TR; MM523003NDB; Manufacturer_Part_Number MM5230-03NDB-TR
J1, J7: Conn_01x02; PinHeader_1x02_P2.54mm_Vertical
J2, J4: Conn_Coaxial; SMA_Molex_73251-1153_EdgeMount_Horizontal
R3: 50; R_0402_1005Metric

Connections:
GND: IC4.4 (RF4), IC4.9 (GND_1), IC4.10 (GND_2), IC4.11 (GND_3), IC4.12 (GND_4), IC4.13 (GND_5), IC4.14 (GND_6), IC4.15 (GND_7), IC4.16 (GND_8), IC4.17 (GND_9), IC4.18 (GND_10), IC4.19 (GND_11), IC4.20 (GND_12), J2.2 (Ext), J4.2 (Ext), R3.1
unnamed: IC4.1 (RF1), J2.1 (In)
unnamed: IC4.5 (RF1GATE), J1.2
unnamed: IC4.2 (RF2), R3.2
unnamed: IC4.6 (RF2GATE), J1.1
unnamed: IC4.3 (RF3), J4.1 (In)
unnamed: IC4.7 (RF3GATE), J7.2
unnamed: IC4.8 (RF4GATE), J7.1

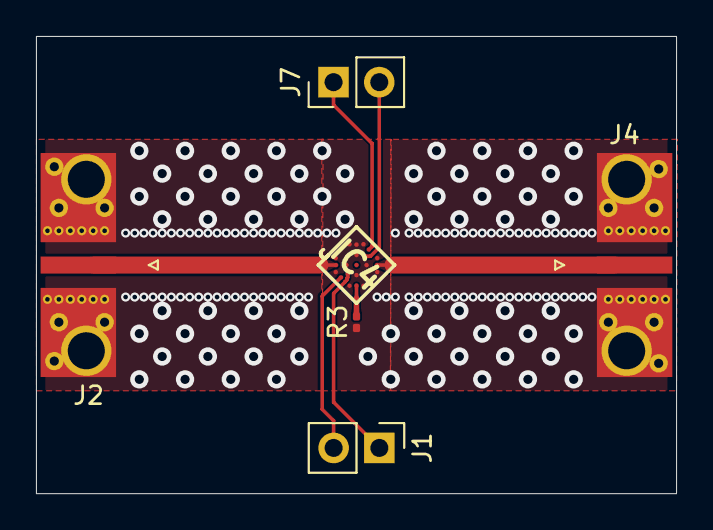
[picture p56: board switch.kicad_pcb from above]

Board: 2 copper layers, 35.6 x 25.4 mm, 6 parts (0 on the bottom side), 8 nets.

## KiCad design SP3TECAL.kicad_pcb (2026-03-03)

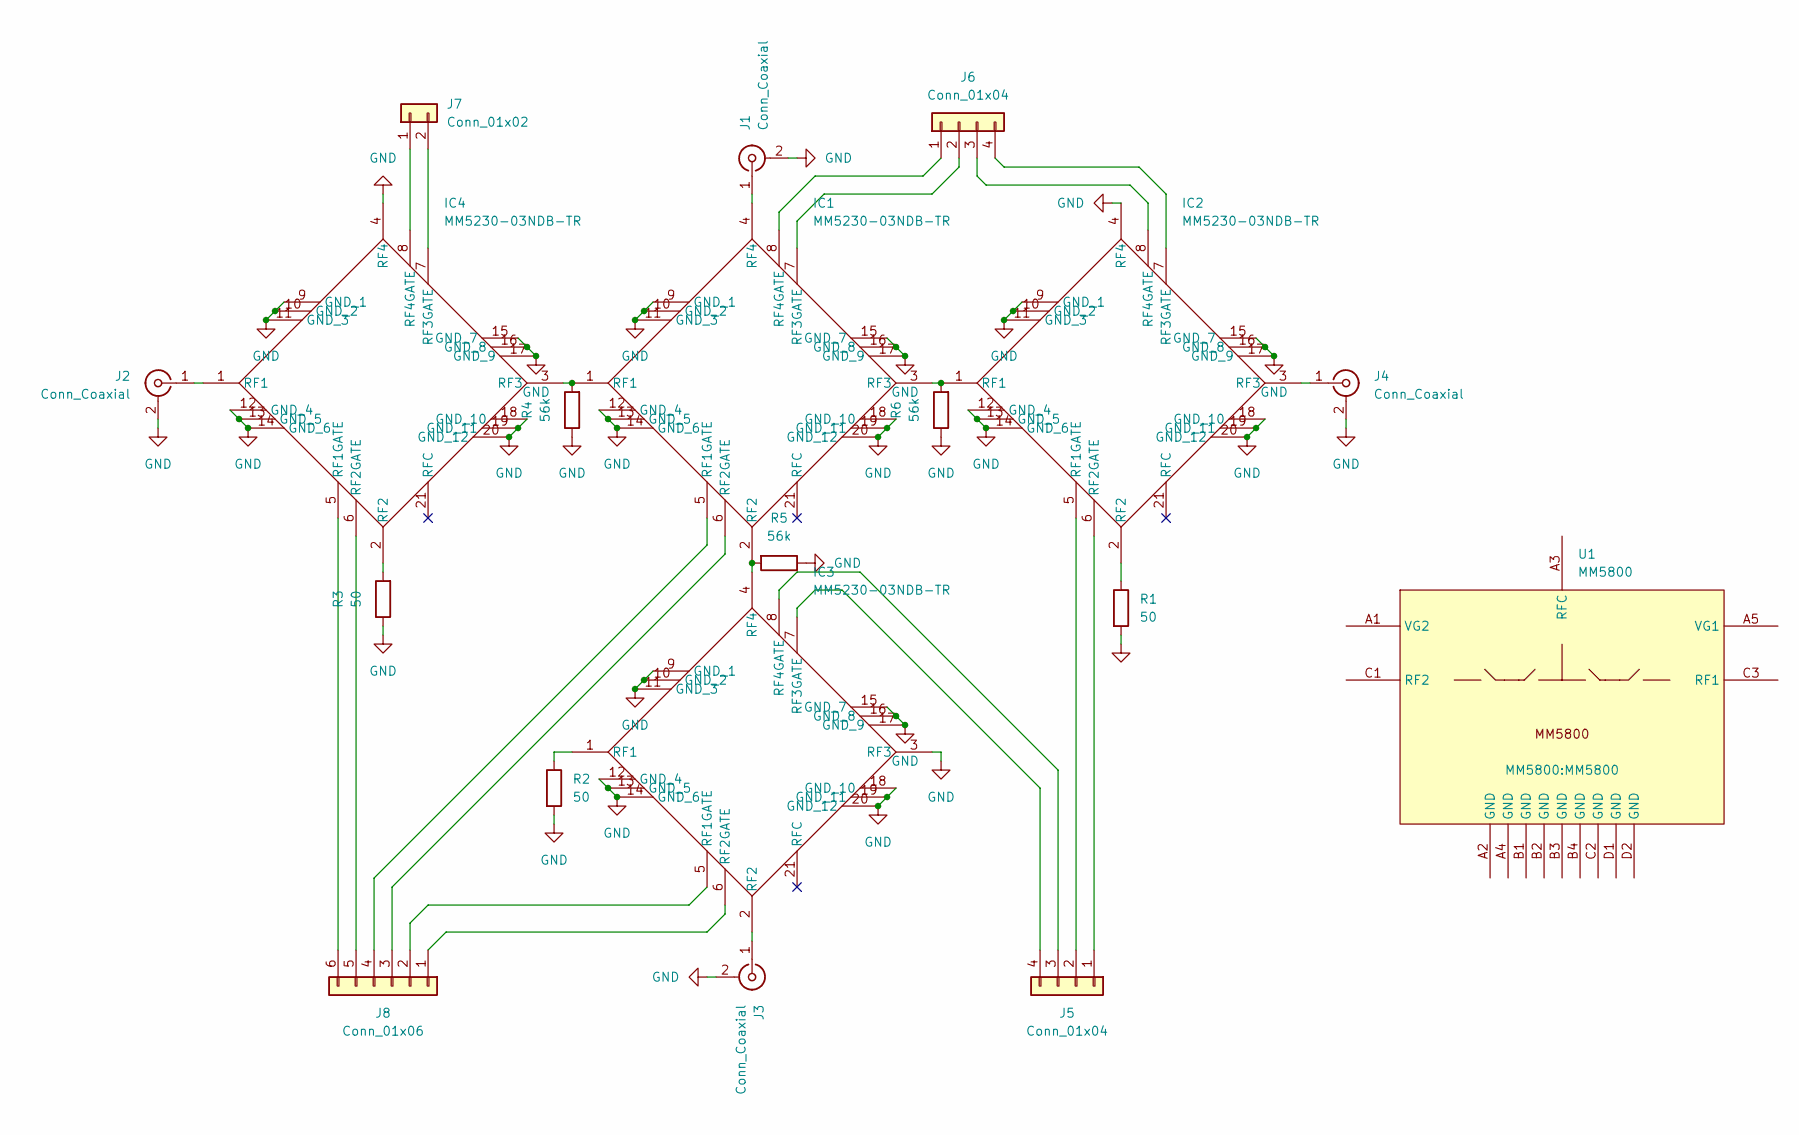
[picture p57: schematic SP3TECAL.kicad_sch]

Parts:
IC1, IC2, IC3, IC4: MM5230-03NDB-TR; MM523003NDB; Manufacturer_Part_Number MM5230-03NDB-TR
J1, J2, J3, J4: Conn_Coaxial; SMA_Molex_73251-1153_EdgeMount_Horizontal
J5, J6: Conn_01x04; PinHeader_1x04_P2.54mm_Vertical
J7: Conn_01x02; PinHeader_1x02_P2.54mm_Vertical
J8: Conn_01x06; PinHeader_1x06_P2.54mm_Vertical
R1, R2, R3: 50; R_0402_1005Metric
R4, R5, R6: 56k; R_0402_1005Metric
U1: MM5800; MANUFACTURER_PART_NUMBER MM5800

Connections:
GND: IC1.9 (GND_1), IC1.10 (GND_2), IC1.11 (GND_3), IC1.12 (GND_4), IC1.13 (GND_5), IC1.14 (GND_6), IC1.15 (GND_7), IC1.16 (GND_8), IC1.17 (GND_9), IC1.18 (GND_10), IC1.19 (GND_11), IC1.20 (GND_12), IC2.4 (RF4), IC2.9 (GND_1), IC2.10 (GND_2), IC2.11 (GND_3), IC2.12 (GND_4), IC2.13 (GND_5), IC2.14 (GND_6), IC2.15 (GND_7), IC2.16 (GND_8), IC2.17 (GND_9), IC2.18 (GND_10), IC2.19 (GND_11), IC2.20 (GND_12), IC3.3 (RF3), IC3.9 (GND_1), IC3.10 (GND_2), IC3.11 (GND_3), IC3.12 (GND_4), IC3.13 (GND_5), IC3.14 (GND_6), IC3.15 (GND_7), IC3.16 (GND_8), IC3.17 (GND_9), IC3.18 (GND_10), IC3.19 (GND_11), IC3.20 (GND_12), IC4.4 (RF4), IC4.9 (GND_1), IC4.10 (GND_2), IC4.11 (GND_3), IC4.12 (GND_4), IC4.13 (GND_5), IC4.14 (GND_6), IC4.15 (GND_7), IC4.16 (GND_8), IC4.17 (GND_9), IC4.18 (GND_10), IC4.19 (GND_11), IC4.20 (GND_12), J1.2 (Ext), J2.2 (Ext), J3.2 (Ext), J4.2 (Ext), R1.2, R2.2, R3.1, R4.1, R5.1, R6.1
unnamed: IC1.1 (RF1), IC4.3 (RF3), R4.2
unnamed: IC1.5 (RF1GATE), J8.4
unnamed: IC1.2 (RF2), IC3.4 (RF4), R5.2
unnamed: IC1.6 (RF2GATE), J8.3
unnamed: IC1.3 (RF3), IC2.1 (RF1), R6.2
unnamed: IC1.7 (RF3GATE), J6.2
unnamed: IC1.4 (RF4), J1.1 (In)
unnamed: IC1.8 (RF4GATE), J6.1
unnamed: IC2.5 (RF1GATE), J5.2
unnamed: IC2.2 (RF2), R1.1
unnamed: IC2.6 (RF2GATE), J5.1
unnamed: IC2.3 (RF3), J4.1 (In)
unnamed: IC2.7 (RF3GATE), J6.4
unnamed: IC2.8 (RF4GATE), J6.3
unnamed: IC3.1 (RF1), R2.1
unnamed: IC3.5 (RF1GATE), J8.2
unnamed: IC3.2 (RF2), J3.1 (In)
unnamed: IC3.6 (RF2GATE), J8.1
unnamed: IC3.7 (RF3GATE), J5.4
unnamed: IC3.8 (RF4GATE), J5.3
unnamed: IC4.1 (RF1), J2.1 (In)
unnamed: IC4.5 (RF1GATE), J8.6
unnamed: IC4.2 (RF2), R3.2
unnamed: IC4.6 (RF2GATE), J8.5
unnamed: IC4.7 (RF3GATE), J7.2
unnamed: IC4.8 (RF4GATE), J7.1

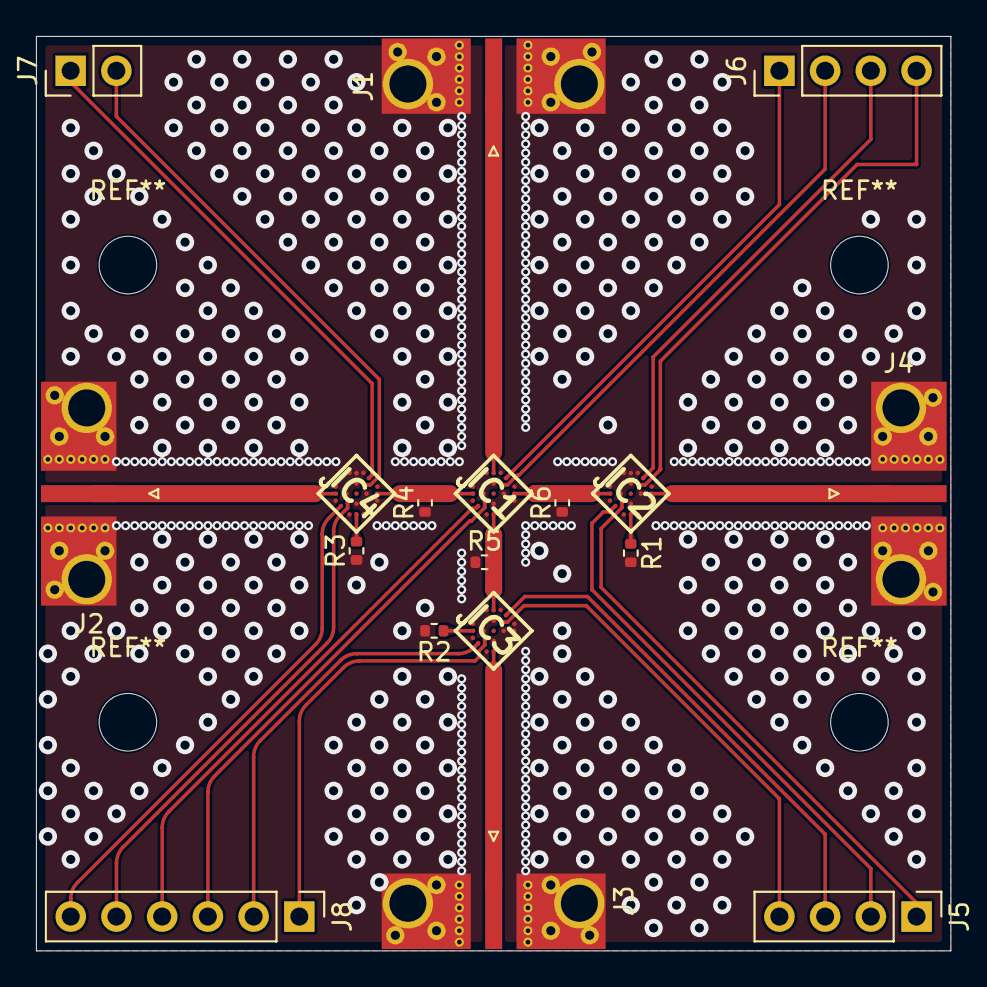
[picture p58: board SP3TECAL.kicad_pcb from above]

Board: 2 copper layers, 50.8 x 50.8 mm, 18 parts (0 on the bottom side), 27 nets.

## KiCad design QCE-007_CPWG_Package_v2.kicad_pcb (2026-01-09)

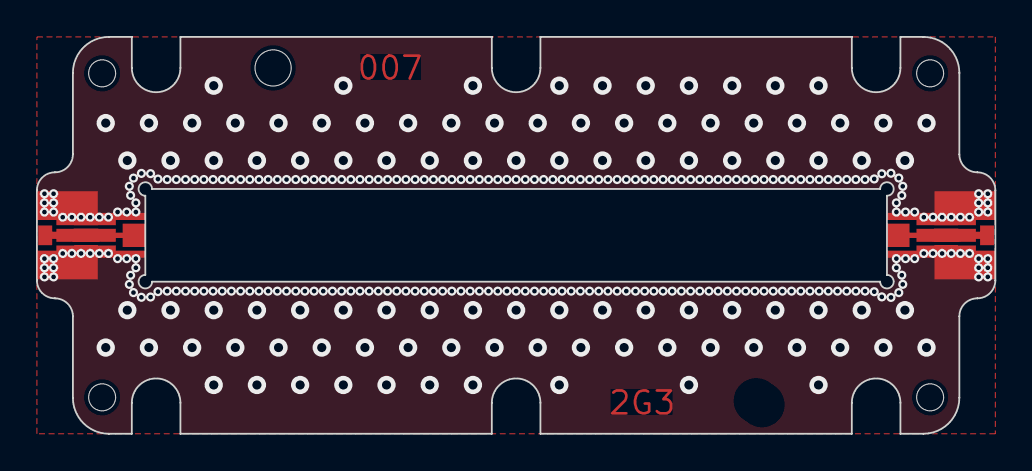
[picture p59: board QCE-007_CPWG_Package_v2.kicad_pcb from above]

Board: 2 copper layers, 53.2 x 22.0 mm, 9 parts (0 on the bottom side), 3 nets.

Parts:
CUTOUT1: CHIP_CUTOUT
DOWEL1, DOWEL2: MOUNTING_HOLE
FID1, FID2, FID3, FID4: MOUNTING_HOLE
J1, J1#2: PANEL

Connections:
1: CUTOUT1.1, J1.1
2: CUTOUT1.2, J1#2.1
GND: CUTOUT1.2, J1.2, J1#2.2

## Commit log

2025-12-20 it's coming together!
    [SP3TECAL.kicad_pcb, SP3TECAL.kicad_sch]
2026-01-09 much progress on routing
    [QCE-007_CPWG_Package_v2.kicad_pcb, SP3TECAL.kicad_pcb, SP3TECAL.kicad_sch]
2026-01-13 adding SOL standards and switch as DUT board
    [CONSMA020.031-G.step, SOL.kicad_pcb, SOL.kicad_sch, SP3TECAL.kicad_pcb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]
2026-01-14 small tweaks on standards boards
    [switch.kicad_pcb]
2026-01-15 made a southwest microwave launch and put it in the thru
    [SP3TECAL.kicad_pcb, thru.kicad_pcb]
2026-01-16 updated SMA launch to SW microwave on all boards
    [SOL.kicad_pcb, SP3TECAL.kicad_pcb, switch.kicad_pcb]
2026-03-03 used altium files to build kicad models of mm5800 and started new twpatron
    [MM5800.PcbDoc, MM5800.SchDoc, SOL.kicad_pcb, SOL.kicad_sch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]
2026-03-03 twpatron added to powerpoint
    [twpatron.kicad_pcb]
2026-03-05 twpatron2 close to a full draft
    [twpatron-2.kicad_pcb, twpatron-2.kicad_sch]
2026-03-06 building 3d models
    [chip-10x20.SLDPRT, twpatron-2-old.SLDPRT, twpatron-2.SLDDRW, twpatron-2.SLDPRT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]
2026-03-09 a full draft of pcb is essentially done now
    [test-board-molex-bias-tee-BOM.xlsx, test-board-molex-bias-tee.PcbDoc, test-board-molex-bias-tee.PrjPcb, test-board-molex-bias-tee.SchDoc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]
2026-03-10 added jaws design, tweaked mechanical for M2.5 screws
    [2VJAWSR6-SMP.PrjPcb, 2VJAWS_RFr60A.PcbDoc, 2VJAWS_RFr60A_Copper_Signal_Bot.gbr, 2VJAWS_RFr60A_Copper_Signal_Top.gbr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]
2026-03-10 changed to stackup like JAWS
    [jaws.kicad_pcb, jaws.kicad_sch, twpatron-2.kicad_pcb]
2026-03-11 twpatron 3d assembly coming together
    [90928A209_Brass Pan Head Slotted Screws.SLDPRT, 93187A112_Brass Thin-Profile Hex Nut.SLDPRT, tpwatron-2-end2.SLDPRT, twpatron-2-b-assembly.SLDASM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]
2026-03-12 finished a draft of the top and bottom combination enclosure
    [tpwatron-2-end2.SLDDRW, tpwatron-2-end2.SLDPRT, twpatron-2-b-assembly.SLDASM, twpatron-2d.SLDDRW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]
2026-03-13 work on pcb layout, lots of small improvements and tweaks
    [twpatron-2.kicad_pcb, twpatron-2e.step]
